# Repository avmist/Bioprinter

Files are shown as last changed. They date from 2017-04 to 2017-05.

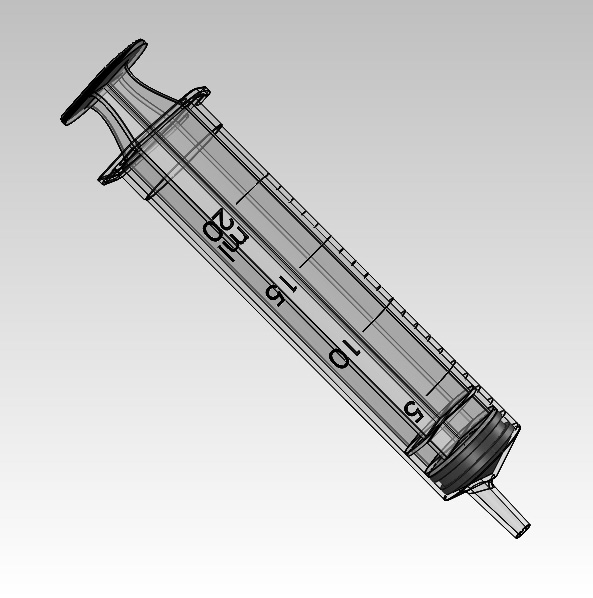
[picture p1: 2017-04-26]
Hardware/Design/Medical/Syringe plastipak-20ml-syringe/Renderings/syringe 20ml plastipak.png

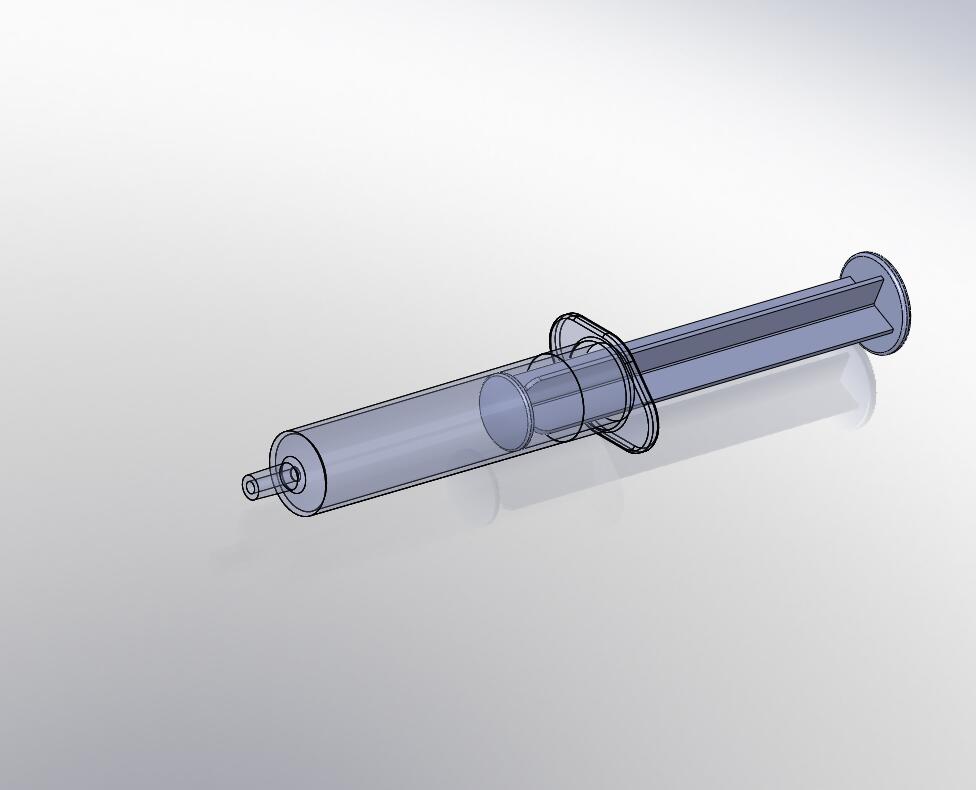
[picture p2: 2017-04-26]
Hardware/Design/Medical/5ml-syringe/Renderings/5ml hsw syringe .jpg

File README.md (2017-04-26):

Add your crew's remote repository, and call it upstream
git remote add upstream https://github.com/UCDBioe3090Blue/Bioprinter.git

Add the Bioe repository, call it headwaters (really, you can call it anything you want)
git remote add headwaters https://UCDBioe3090Blue@github.com/UCDBioe/Bioprinter.git

Pull the headwaters remote into your local repo
git pull headwaters master
git fetch headwaters master
git diff master headwaters/master
git diff --name-only master headwaters/master
git merge headwaters/master 

Pull the upstream remote into your local repo
git pull upstream master

Push updated local repo to origin
git push origin master

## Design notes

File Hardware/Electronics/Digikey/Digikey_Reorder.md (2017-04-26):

Bioprinter - BOM
================

## Digikey
-------------

Per Syringe Extruder
--------------------
Quantity  |   Part Number   |   Description                     
----------|-----------------|-----------------------------------
4         |  FQP30N06L-ND   |  MOSFET                           
4         |  DS18B20+-ND    |  TempSensor                       

Wire Harness
------------
Quantity  |   Part Number   |   Description                     
----------|-----------------|-----------------------------------
30        |  455-1130-1-ND  |  ZH_Connector_Socket              
10        |  455-1160-ND    |  ZH_Female                        
10        |  455-1658-ND    |  ZH_Male_pin_Solder               
30        |  WM2901-ND      |  Molex_3pos_female                
30        |  WM2562CT-ND    |  Molex_Connector_Socket_Crimp     
60        |  WM2513-ND      |  Molex_Connector_Socket_Crimp_Gold
30        |  WM2534-ND      |  Molex_3pos_male                  
30        |  WM2565CT-ND    |  Molex_Connector_Pin_Crimp        
60        |  WM2516-ND      |  Molex_Connector_Pin_Crimp_Gold   
30        |  WM2900-ND      |  Power_Plug                       
60        |  WM2512CT-ND    |  Female_Socket_Crimp              
30        |  WM2533-ND      |  Power_Housing_Male               
60        |  WM2515CT-ND    |  Male_Pin_Crimp                   
1         |  6820 BK005-ND  |  28AWG_Stranded_BLK               
1         |  6820 RD005-ND  |  28AWG_Stranded_RED               
1         |  6820 YL005-ND  |  28AWG_Stranded_YEL               
1         |  6823 BK005-ND  |  22AWG_Stranded_BLK               
1         |  6823 RD005-ND  |  22AWG_Stranded_RED               
1         |  6823 GR005-ND  |  22AWG_Stranded_GRN               
1         |  6823 BL005-ND  |  22AWG_Stranded_BLU               
20        |  WM2873-ND      |  Molex_StepperMotor_Connector     
80        |  WM2510-ND      |  Stepper_Motor_Connector_Terminal 
1         |  ASW40-25-ND    |  1/8in_Spiral_Wrap                

UV-LED
------
1         |  1125-1254-ND   |  30mA 365nm 
1         |  1214-1322-ND   |  A 365nm

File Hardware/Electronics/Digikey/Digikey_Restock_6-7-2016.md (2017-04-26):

Bioprinter - BOM
================

## Digikey
-------------

Per Syringe Extruder
--------------------
Quantity  |   Part Number   |   Description                     
----------|-----------------|-----------------------------------                        
4         |  DS18B20+-ND    |  TempSensor                       

Wire Harness
------------
Quantity  |   Part Number   |   Description                     
----------|-----------------|-----------------------------------           
20        |  WM2901-ND      |  Molex_3pos_female                     
30        |  WM2513-ND      |  Molex_Connector_Socket_Crimp_Gold
20        |  WM2534-ND      |  Molex_3pos_male                       
30        |  WM2516-ND      |  Molex_Connector_Pin_Crimp_Gold   
10        |  WM2900-ND      |  Power_Plug                       
20        |  WM2512CT-ND    |  Female_Socket_Crimp              
10        |  WM2533-ND      |  Power_Housing_Male               
20        |  WM2515CT-ND    |  Male_Pin_Crimp                   
1         |  6820 BK005-ND  |  28AWG_Stranded_BLK               
1         |  6820 RD005-ND  |  28AWG_Stranded_RED               
1         |  6820 YL005-ND  |  28AWG_Stranded_YEL               
1         |  6823 BK005-ND  |  22AWG_Stranded_BLK               
1         |  6823 RD005-ND  |  22AWG_Stranded_RED               
             
1         |  ASW40-25-ND    |  1/8in_Spiral_Wrap                

UV-LED
------
1         |  1125-1254-ND   |  30mA 365nm 
1         |  1214-1322-ND   |  A 365nm

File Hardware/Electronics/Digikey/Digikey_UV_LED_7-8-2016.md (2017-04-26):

Quantity  |   Part Number               |   Description                   
----------|-----------------------------|---------------------------------
2         |  1537-1032-ND               |  EMITTER UV 365NM 1A STAR       
2         |  1168-2129-ND               |  12x12x10 Ceramic Heatsink      
2         |  1284-1346-1-ND             |  Heat Spreader                  
1         |  MLX90614ESF-ACF-000-TU-ND  |  IR Temperature Sensor          
4         |  A98333-ND                  |  TERM BLOCK 2POS SIDE ENT 2.54MM
4         |  ED10561-ND                 |  CONN TERM BLOCK 2.54MM 2POS PCB

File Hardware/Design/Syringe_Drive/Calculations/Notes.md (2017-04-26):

Stepper Motor Spur Gear
-----------------------
Part Number: S10T08M012S0505
Pitch Diameter 9.6 mm
With Hub and Set screw
Module 0.8 teeth/mm
12 Teeth
20° Pressure Angle
303 Stainless Steel Gear
https://sdp-si.com/eStore/Catalog/Group/591#

Large Gear mates with Stepper Motor Spur Gear
---------------------------------------------

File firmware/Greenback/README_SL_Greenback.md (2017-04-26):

Changes and Notes for Bioprinter Greenback (Barlin)
=======================================

By Steve Lammers

Notes and Stuff To Do
=====================
*  **Fix printer bed size, currently too small**
*  **ADVANCE in stepper.cpp, use this to define a new method for BIOADVANCE**

Printer Details
===============
 *  AO-100 (not AO-101)
 *  RAMPS 1.4 board
 *  Arduino MEGA 2560 micro
 *  See link at LulzBot for [details](http://download.lulzbot.com/AO-100) 

Configure Greenback for AO-100 printer
===================================
AP-100 Printer is based on the RAMPS1.4 board with an extruder, bed and fan power. Change the following code in Configuration.h 

`BASIC SETTINGS: select your board type, temperature sensor type, axis scaling, and endstop configuration`

    // The following define selects which electronics board you have.
    // Please choose the name from boards.h that matches your setup
    #ifndef MOTHERBOARD
    //#define MOTHERBOARD BOARD_ULTIMAKER
    #define MOTHERBOARD BOARD_RAMPS_13_EFB
    #endif
    
The name 'BOARD_RAMPS_13_EFB' found in the boards.h file.

Baud Rate
---------
    // This determines the communication speed of the printer
    #define BAUDRATE 115200 //250000

Thermal Settings
----------------
    #define TEMP_SENSOR_0 7
    #define TEMP_SENSOR_1 0
    #define TEMP_SENSOR_2 0
    #define TEMP_SENSOR_BED 7

Mechanical Settings
-------------------
Set the direction that the stepper motors move the gantry

    #define INVERT_X_DIR false    // for Mendel set to false, for Orca set to true
    #define INVERT_Y_DIR true    // for Mendel set to true, for Orca set to false
    #define INVERT_Z_DIR false     // for Mendel set to false, for Orca set to true
    #define INVERT_E0_DIR true   // for direct drive extruder v9 set to true, for geared extruder set to false
    #define INVERT_E1_DIR false    // for direct drive extruder v9 set to true, for geared extruder set to false
    #define INVERT_E2_DIR false   // for direct drive extruder v9 set to true, for geared extruder set to false

Define endstop inverting

    // The pullups are needed if you directly connect a mechanical endswitch between the signal and ground pins.
    const bool X_MIN_ENDSTOP_INVERTING = false; // set to true to invert the logic of the endstop.
    const bool Y_MIN_ENDSTOP_INVERTING = false; // set to true to invert the logic of the endstop.
    const bool Z_MIN_ENDSTOP_INVERTING = false; // set to true to invert the logic of the endstop.
    const bool X_MAX_ENDSTOP_INVERTING = false; // set to true to invert the logic of the endstop.
    const bool Y_MAX_ENDSTOP_INVERTING = false; // set to true to invert the logic of the endstop.
    const bool Z_MAX_ENDSTOP_INVERTING = false; // set to true to invert the logic of the endstop.

Define manual homing position

    // The position of the homing switches
    #define MANUAL_HOME_POSITIONS  // If defined, MANUAL_*_HOME_POS below will be used
    //#define BED_CENTER_AT_0_0  // If defined, the center of the bed is at (X=0, Y=0)

Endstop Config
--------------
    #define min_software_endstops true // If true, axis won't move to coordinates less than HOME_POS.
    #define max_software_endstops true  // If true, axis won't move to coordinates greater than the defined lengths below.
    
    // Travel limits after homing
    #define X_MAX_POS 200
    #define X_MIN_POS 0
    #define Y_MAX_POS 190
    #define Y_MIN_POS 0
    #define Z_MAX_POS 100
    #define Z_MIN_POS 0

Axis Scaling
------------
    #define DEFAULT_AXIS_STEPS_PER_UNIT   {44.7,44.7,1512,800}  // default steps per unit for Ultimaker
    #define DEFAULT_MAX_FEEDRATE          {800, 800, 10, 500}    // (mm/sec)
    #define DEFAULT_MAX_ACCELERATION      {9000,9000,100,10000}    // X, Y, Z, E maximum start speed for accelerated 

Flashing the Firmware
======================
 *  Use Arduino 1.0.1 or 1.0.5
 *  Use Arduino MEGA 2560 board
 *  Use correct Greenback version for the AO-100 printer
 *  Electronics board in the Configuration.h set to 33 (RAMPS 1.3 = 33 (Power outputs: Extruder, Bed, Fan))
 *  In Configuration.h: #define DEFAULT_AXIS_STEPS_PER_UNIT   {50.25,50.25,756.00,408.00}  // default steps per unit for ultimaker 
 *  May need to set X_MAX_LENGTH, etc for the size of the bed????
 *  Need to use current version of Greenback if we are going to use multiple extruders!!!!!!!!!!!!!!!!!

Pin Definitions for Test LED
============================
###In pinsBioprinter.h

E0 LED Pin is on Aux-4 pin 3: `#DEFINE E0_LED_PIN 32 // Digital Pin 32 on AUX-4` 

###In Greenback_main.cpp

Initialize Pins: `pinMode(E0_LED_PIN, OUTPUT);`

###In Stepper.cpp and Stepper.h

Define WRITE_E_LED() to toggle LED during extrusion

Configure for BioExtruders
=============================
###In Configuration.h
* define BIOEXTRUDERS 2 // Defines the number of bioextruders

Copy and alter Stepper.h and Stepper.cpp to BioValve.h and BioValve.cpp

In pinsBioprinter.h
`define BIOPRINT 1 // 1-enables bioprint, 0-enables filament`
Set BIOPRINT to 1 when a bioprint tool is selected, set it to 0 when a filament tool is selected

In Greenback_main.cpp: Define tools T0-T9 as filament extruders and T10-T19 as bio-print heads. When T0-T9 is selected set BIOPRINT = 0, when T10-T19 is selected set BIOPRINT to 1.

Use BIOPRINT to govern how extrusion is done in stepper.cpp and stepper.h. Since this contains the ISR which is used in all of the printing, keep using G1 E codes for printing. Change to bioprint heads using T codes, and flag what material is being printed (bio or plastic) using BIOPRINT.

plan_buffer_line()
===================
`void plan_buffer_line(const float &x, const float &y, const float &z, const float &e, float feed_rate, const uint8_t &extruder)`

target[]: rounded total steps in x,y,z,e-direction
`target[X_AXIS] = lround(x*axis_steps_per_unit[X_AXIS]);`

Prevent dangerous extrude code follows

define total absolute steps to move stepper motors for each axis i.e.:
`block->steps_x = labs(target[X_AXIS]-position[X_AXIS]);`

`block->steps_e` has some additional code, basically: `steps_e/(pi R^2)*100/100` where R is filament diameter, basically normalizes thin and thick filament feedrates. **Will need to add to this for bioprinter**

```
  block->steps_e = labs(target[E_AXIS]-position[E_AXIS]);
  block->steps_e *= volumetric_multiplier[active_extruder];
  block->steps_e *= extrudemultiply;
  block->steps_e /= 100;
```

step_event_count is the max step size for x,y,z,e directions 
`block->step_event_count = max(block->steps_x, max(block->steps_y, max(block->steps_z, block->steps_e)));`

Fan Speed `block->fan_speed = fanSpeed;`

Stuff for BAEICUDA

```
  #ifdef BARICUDA
  block->valve_pressure = ValvePressure;
  block->e_to_p_pressure = EtoPPressure;
  #endif
```
Compute direction bits for this block `block->direction_bits = 0;`, then shift in bits in the LSB for X,Y,Z,E direction 0 or 1

Set active extruder
`block->activer_extruder = extruder;`

Ennable active axes

```
  if(block->steps_x != 0) enable_x();
  if(block->steps_y != 0) enable_y();
```

Enable extruder(s)
This code ensures that only the active extruder is enabled if DISABLE_INACTIVE_EXTRUDER is defined (which it is by default). **Will need to add to this for bioprinters?**

Calculate the total length of the movement. For cartesian bots, the `X_AXIS` is the real X movement and same for `Y_AXIS`.

```
  float delta_mm[4];
  delta_mm[X_AXIS] = (target[X_AXIS]-position[X_AXIS])/axis_steps_per_unit[X_AXIS];
  delta_mm[Y_AXIS] = (target[Y_AXIS]-position[Y_AXIS])/axis_steps_per_unit[Y_AXIS];
  delta_mm[Z_AXIS] = (target[Z_AXIS]-position[Z_AXIS])/axis_steps_per_unit[Z_AXIS];
  delta_mm[E_AXIS] = ((target[E_AXIS]-position[E_AXIS])/axis_steps_per_unit[E_AXIS])*volumetric_multiplier[active_extruder]*extrudemultiply/100.0;
  if ( block->steps_x <=dropsegments && block->steps_y <=dropsegments && block->steps_z <=dropsegments )
  {
    block->millimeters = fabs(delta_mm[E_AXIS]);
  } 
  else
  {
    block->millimeters = sqrt(square(delta_mm[X_AXIS]) + square(delta_mm[Y_AXIS]) + square(delta_mm[Z_AXIS]));
  {
  float inverse_millimeters = 1.0/block->millimeters;  // Inverse millimeters to remove multiple divides 

    // Calculate speed in mm/second for each axis. No divide by zero due to previous checks.
  float inverse_second = feed_rate * inverse_millimeters;

  int moves_queued=(block_buffer_head-block_buffer_tail + BLOCK_BUFFER_SIZE) & (BLOCK_BUFFER_SIZE - 1);
```

In configuration.h, SLOWDOWN defined as default. inverse_second is redeined to slow down when the look ahead
buffer is only half full

Calculate the speedin mm/sec and the step-rate in step/sec

```
block->nominal_speed = block->millimeters * inverse_second; // (mm/sec) Always > 0
block->nominal_rate = ceil(block->step_event_count * inverse_second); // (step/sec) Always > 0
```

Calculate `current_speed` in mm/sec for each axis and `speed_factor <=1` for the minimum of either 1 or max_feedrate/current_speed

XY_FREQUENCY_LIMIT not defined by default

Speed is corrected using speed_factor

```
  // Correct the speed  
  if( speed_factor < 1.0)
  {
    for(unsigned char i=0; i < 4; i++)
    {
      current_speed[i] *= speed_factor;
    }
    block->nominal_speed *= speed_factor;
    block->nominal_rate *= speed_factor;
  }
```

Calculate acceleration and save to block

```
block->acceleration_st
block->acceleration
block->acceleration_rate
```

Correct for jerking due to high acceleration

```
block->max_entry_speed
block->entry_speed
block->normal_length_flag
block->recalculate_flag
```

Calculate trapezoid for the block, move buffer head, update position and wake up the stepper motors

```
calculate_trapezoid_for_block(block, block->entry_speed/block->nominal_speed,
safe_speed/block->nominal_speed);

// Move buffer head
block_buffer_head = next_buffer_head;

// Update position
memcpy(position, target, sizeof(target)); // position[] = target[]

planner_recalculate();

st_wake_up();
```
st_wake_up called in stepper.cpp
***END PLAN BUFFER LINE***

Timers
======
Timers all have something in Greenback_main.cpp
* Timer0 ????? Pins 1 and 26
* Timer1 - stepper.cpp
* Timer2 ????? Pins 16 and 23 are open on AUX-4
* Timer3 - servo.h
* Timer4 - servo.h
* Timer5 - servo.h

Extruder Offsets
================
Need to figure out how to have the firmware apply offsets for each of the bio-extruders.

```
// Offset of the extruders (uncomment if using more than one and relying on firmware to position when changing).
// The offset has to be X=0, Y=0 for the extruder 0 hotend (default extruder).
// For the other hotends it is their distance from the extruder 0 hotend.
#define EXTRUDER_OFFSET_X {0.0, 10.00} // (in mm) for each extruder, offset of the hotend on the X axis
#define EXTRUDER_OFFSET_Y {0.0, 5.00}  // (in mm) for each extruder, offset of the hotend on the Y axis
```

In Greenback_main.cpp

```
// Extruder offset
#if EXTRUDERS > 1 || defined(BIOEXTRUDERS) //SL Note: Added BIOEXTRUDERS to account for offset
#ifndef DUAL_X_CARRIAGE
  #define NUM_EXTRUDER_OFFSETS 2 // only in XY plane
#else
  #define NUM_EXTRUDER_OFFSETS 3 // supports offsets in XYZ plane
#endif
//float extruder_offset[NUM_EXTRUDER_OFFSETS][EXTRUDERS] = {
float extruder_offset[NUM_EXTRUDER_OFFSETS][10+BIOEXTRUDERS] = { //SL Note: Added 10 to account for Filament extruders 0-9
#if defined(EXTRUDER_OFFSET_X) && defined(EXTRUDER_OFFSET_Y)
  EXTRUDER_OFFSET_X, EXTRUDER_OFFSET_Y 
#endif
};
```

So `extruder_offset` is a 3xn array where n = 10+BIOEXTRUDERS. BIOEXTRUDERS is the number of bioextruders, 10+ is the number of possible filament printheads. Of course this is much higher than the actual number the RepRap could support, but it was chosen such the T10 would be the first bioprint head. So to make this work, fill in the `EXTRUDER_OFFSET_X` and `EXTRUDER_OFFSET_Y` arrays in Configuration.h

```
#define EXTRUDER_OFFSET_X {0.0, 0.0, 0.0, 0.0, 0.0, 0.0, 0.0, 0.0, 0.0, 0.0, 10.0} // (in mm) for each extruder, offset of the hotend on the X axis
#define EXTRUDER_OFFSET_Y {0.0, 0.0, 0.0, 0.0, 0.0, 0.0, 0.0, 0.0, 0.0, 0.0, 5.00}  // (in mm) for each extruder, offset of the hotend on the Y axis
```

Now when the tool is changed, say to bioprinthead[0] using T10 command, the `current_position` array is updated to reflect the new printhead. So if `EXTRUDER_OFFSET_X[10]=10` and `current_position[0]=100` before the tool was changed, after issuing T10 command `current_position=110`, because `EXTRUDER_OFFSET_X[10]=10`. However, the printer stage does not move, the position will be reflected at the next move command. If you want to change printheads and begin printing at the same point with the new printhead, you will need to resend the position command using G1.

Removal of Existing Extruder
=============================
The existing extruder and part heating pad needs to be removed. When the extruder heater is disconnected, the printer throws an error "Printer stopper due to errors. Fix the error and use M999 to reset. (Temperature is reset. Set it after restatring)". This happened because the Stop() function was called. To correct this, use an existing override by adding the following to pinsBioprinter.h

'''
// This definition is used to turn off the physical checks on thermister
// readings, typically set in pins.h. T0 and T1 thermistors provided temperature data for
// the extruder and heated bed respectively. These thermistors are disconnected
// for the bioprinter. So we can ignore the associated errors using this definition
#define BOGUS_TEMPERATURE_FAILSAFE_OVERRIDE
// Temperature errors persist, set TEMP_SENSOR_0 = 0 AND TEMP_SENSOR_BED = 0 in Configuration.h
'''

Temperature errors persist. Set in Configuration.h

'''
#define TEMP_SENSOR_0 0 // 7 Setting for Lulzbot AO-100
#define TEMP_SENSOR_1 0
#define TEMP_SENSOR_2 0
#define TEMP_SENSOR_BED 0 // 7 Setting for Lulzbot AO-100
'''

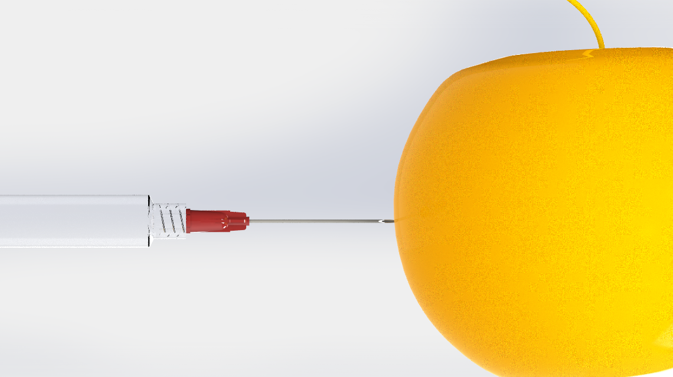
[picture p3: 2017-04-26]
Hardware/Design/Medical/hypodermic-syringe-1.snapshot.3/Renderings/syringe apple.PNG

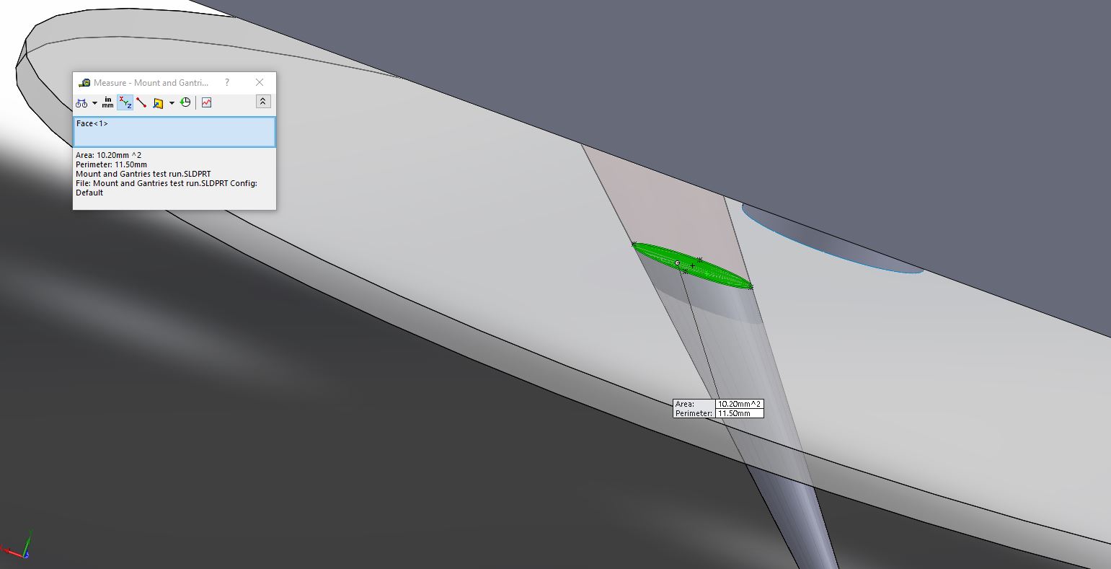
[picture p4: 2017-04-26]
Hardware/Design/Needle_Mount/Square_Carrige/IR sensor area covered.JPG

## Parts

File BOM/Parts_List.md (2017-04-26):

---------------------------------------------------
Additional Optional Equipment not Purchased for This Model
==========================
***
Digital Pressure Regulator
==========================
###[IPV-2010RC](http://www.smcpneumatics.com/ITV2010-31N2N4.html) - Digital pressure sensor
* Min supply pressure: .1 MPa (14.5 psi)
* Max supply pressure: .2 MPa
* Set pressure range: .005 - .1 MPa (0.725 - 14.5 psi)
* Input Signal: 0-5 VDC or RS-232
* Minimum Digit: 0.1 psi
* Accuracy: 0.2% Full Span +/- 1 digit
	* 0.002 * (14.5 - 0.725)psi = 0.03psi

###[IPV-1000](http://www.smcpneumatics.com/ITV2010-31N2N4.html) - Digital pressure sensor
* Min supply pressure: .1 MPa (14.5 psi)
* Max supply pressure: .2 MPa
* Set pressure range: .001 - .1 MPa (0.145 - 14.5 psi)
* Input Signal: 0-5 VDC ***only***
* Minimum Digit: 0.1 psi
* Accuracy: 0.2% Full Span +/- 1 digit
	* (.002 * (14.5 - 0.145)psi) = 0.02psi

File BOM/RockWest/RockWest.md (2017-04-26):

Bioprinter - BOM
================

## Rock West Composites
-----------------------

Carbon Fiber Sleeves for Tubing Heaters
---------------------------------------
Quantity  |  Part Number  |  Description                             
----------|---------------|------------------------------------------
10        |  BR-C-050     |  Dry Braided Sleeve - Carbon Fiber - 0.5"

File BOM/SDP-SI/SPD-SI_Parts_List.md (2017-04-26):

SDP-SI - BOM
============
## For Each Syringe Drive
-------------------------

Quantity  |  Part Number       |  Description                                                                                      
----------|--------------------|---------------------------------------------------------------------------------------------------
1         |  A 7X 1-06012      |  .18720" (+.000/-.0002) Dia. 1.25" Long 303 Stainless Steel Shaft                                 
2         |  A 7X 1-04023      |  .12470" (+.000/-.0002) Dia. 2.375" Long 303 Stainless Steel Shaft                                
1         |  A 7X 8-C04031     |  0.125" I.D. 0.1875" O.D. 0.031" Thick Shaft Spacer                                               
3         |  A 7X 8-C04016     |  0.125" I.D. 0.1875" O.D. 0.016" Thick Shaft Spacer                                               
1         |  S5000Y-12510      |  0.1248" Bore 0.3125" O.D. 0.18" Wide 303 Stainless Steel Collar Style                            
1         |  A 1T 2-Y32016     |  32 DP 16 Teeth 20° Pressure Angle Acetal / Brass insert spur Gear                                
1         |  S1C83Z-P048B055S  |  55:1 Gear Ratio 55 Teeth Worm Gear                                                               
1         |  S1D94Z-P048SS     |  48DP/1 Lead/.33PD 20° Pressure Angle Stainless Steel Worm                                        
1         |  S1063Z-048A024    |  48 D.P. 24 Teeth 20° Pressure Angle AGMA Q10 Quality With ( Hub / S.S.) 2024 Aluminum Alloy Gear.
1         |  S1063Z-048S048    |  48 D.P. 48 Teeth 20° Pressure Angle AGMA Q10 Quality With ( Hub / S.S.) 303 Stainless Steel Gear.

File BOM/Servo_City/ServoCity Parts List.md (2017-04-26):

Servo City - BOM
================
## For Each Syringe Drive
-------------------------

Mostly Actobotics Parts are needed. Some of the gears are not available on Servo City. These components were sourced from SDP/SI

Quantity  |  Part Number  |  Description                                      |  Unit Price  |  Total 
----------|---------------|---------------------------------------------------|--------------|--------
1         |  585442       |  3.00 inch Aluminum Channel                       |  3.99        |  3.99  
1         |  555152       |  Stepper Motor Mount (NEMA 17)                    |  7.49        |  7.49  
1         |  625176       |  3/16 inch to 5mm Set Screw Shaft Coupler         |  4.99        |  4.99  
1         |  634136       |  3/16 inch x1 inch Precision Shaft                |  0.49        |  0.49  
1         |  634138       |  3/16 inch x2 inch Precision Shaft                |  0.69        |  0.69  
2         |  633138       |  Center Hole Adaptors (4 pack)                    |  1.99        |  3.98  
2         |  535206       |  1/8 inch ID x 3/8 inch OD Ball Bearing (2 pack)  |  1.99        |  3.98  
1         |  545424       |  90 Degree Quad Hub Mount B                       |  4.99        |  4.99  
1         |  585656       |  Beam Bracket T (Pair)                            |  1.49        |  1.49  
1         |  585600       |  Beam Attachment Block B (4 pack)                 |  4.99        |  4.99  
1         |  585416       |  6.16 inch Aluminum Beam (2 pack)                 |  5.49        |  5.49  
1         |  615410       |  32P Beam Gear Rack                               |  5.99        |  5.99  
2         |  585434       |  1 inch Bore Tube Clamp A                         |  5.99        |  11.98 
1         |  585612       |  Beam Bracket F (Pair)                            |  1.49        |  1.49  
1         |  585404       |  1.54 inch Aluminum Beam (2 pack)                 |  2.39        |  2.39  
1         |  585490       |  Beam Crossover Adaptor A                         |  2.99        |  2.99  
1         |  585400       |  Attachment Blocks (12 pack)                      |  9.99        |  9.99  
1         |  545360       |  90 Degree Quad Hub Mount C                       |  5.99        |  5.99  
1         |  632146       |  Actobotics Hardware Pack A                       |  39.99       |  39.99 
1         |  632148       |  Hardware Pack B                                  |  10.99       |  10.99 
4         |  534-3488     |  6-32x .750 inch Aluminum Standoffs (Round)       |  0.45        |  1.80

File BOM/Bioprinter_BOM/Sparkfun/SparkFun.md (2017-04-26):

Bioprinter - BOM
================

## Spark Fun
-------------

Per Syringe Extruder
--------------------
Quantity  |  Part Number  |  Description                                    
----------|---------------|-------------------------------------------------
1         |  COM-10080    |  Thermoelectric Cooler 40x40mm                  
1         |  COM-11288    |  Heating Pad - 5x10cm                           
5         |  PRT-09915    |  JSST Jumper 3 Wire Assembly                    
1         |  PRT-10811    |   DC Barrel Jack Adapter - Breadboard Compatible
5         |  SEN-08733    |  Infrared Sensor Jumper Wire 3-Pin JST

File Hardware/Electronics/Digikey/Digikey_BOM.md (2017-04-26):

Bioprinter - BOM
================

## Digikey
-------------

Per Syringe Extruder
--------------------
Quantity  |   Part Number   |   Description                     
----------|-----------------|-----------------------------------
4         |  FQP30N06L-ND   |  MOSFET                           
1         |  438-1046-ND    |  Breadboard                       
4         |  DS18B20+-ND    |  TempSensor                       
1         |  1050-1041-ND   |  Arduino_UNO                      
1         |  T1171-P5RP-ND  |  Power_Adapter_5V_3.6A            
1         |  839-1219-ND    |  Barrel_Jack_to_Gator

Wire Harness
------------
Quantity  |   Part Number   |   Description                     
----------|-----------------|-----------------------------------
30        |  455-1130-1-ND  |  ZH_Connector_Socket              
10        |  455-1160-ND    |  ZH_Female                        
10        |  455-1658-ND    |  ZH_Male_pin_Solder               
30        |  WM2901-ND      |  Molex_3pos_female                
30        |  WM2562CT-ND    |  Molex_Connector_Socket_Crimp     
60        |  WM2513-ND      |  Molex_Connector_Socket_Crimp_Gold
30        |  WM2534-ND      |  Molex_3pos_male                  
30        |  WM2565CT-ND    |  Molex_Connector_Pin_Crimp        
60        |  WM2516-ND      |  Molex_Connector_Pin_Crimp_Gold   
30        |  WM2900-ND      |  Power_Plug                       
60        |  WM2512CT-ND    |  Female_Socket_Crimp              
30        |  WM2533-ND      |  Power_Housing_Male               
60        |  WM2515CT-ND    |  Male_Pin_Crimp                   
1         |  6820 BK005-ND  |  28AWG_Stranded_BLK               
1         |  6820 RD005-ND  |  28AWG_Stranded_RED               
1         |  6820 YL005-ND  |  28AWG_Stranded_YEL               
1         |  6823 BK005-ND  |  22AWG_Stranded_BLK               
1         |  6823 RD005-ND  |  22AWG_Stranded_RED               
1         |  6823 GR005-ND  |  22AWG_Stranded_GRN               
1         |  6823 BL005-ND  |  22AWG_Stranded_BLU               
20        |  WM2873-ND      |  Molex_StepperMotor_Connector     
80        |  WM2510-ND      |  Stepper_Motor_Connector_Terminal 
1         |  ASW40-25-ND    |  1/8in_Spiral_Wrap                

Extras
------
1         |  1050-1018-ND   |  ArduinoMega                      
1         |  Q2F1-KIT-ND    |  HeatShrink_Kit                   
1         |  8331S-15G      |  Conductive Epoxy 10min work time 

Peltier
-------
1         |  ATS1758-ND     |  Heat Sink 
1         |  3M12011-ND     |  Thermal Tape 

Blower
------
1         |  603-1370-ND    |  Squirrel Cage Blower 

UV-LED
------
1         |  1125-1254-ND   |  30mA 365nm 
1         |  1214-1322-ND   |  A 365nm 

Also Needed
------------------------------
* Engineer PA-09 Crimp tool
* Paladin Grip P20 Wire Stripper

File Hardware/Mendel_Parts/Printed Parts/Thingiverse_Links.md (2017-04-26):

Parts on Thingiverse
--------------------
* [X-carrige](hrome-extension://hdokiejnpimakedhajhdlcegeplioahd)
* [Frame Brackets](http://www.thingiverse.com/thing:97575)

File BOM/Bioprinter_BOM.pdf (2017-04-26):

ID | Part Name | Vendor Number | Quantity | Description | Photo

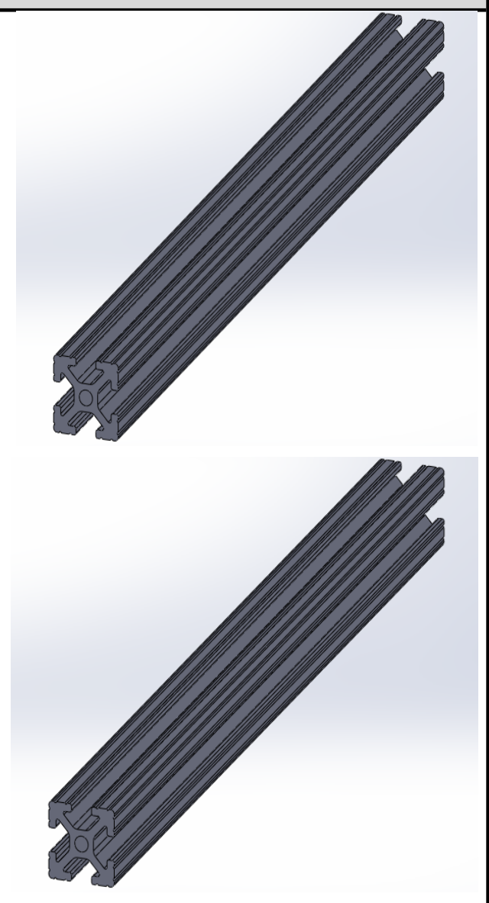
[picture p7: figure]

A1

Aluminum Extrusion
80/20 Size 20-2020
Cut to 265 mm long
Tapped M5 x 0.8 bolt

Misumi
HFS5-2020-265-TPW 4

T-Slotted Frame
Shortest
(x-axis)

A2

Aluminum Extrusion
80/20 Size 20-2020
Cut to 300 mm long
Tapped M5 x 0.8 bolt

Misumi
HFS5-2020-300-TPW 4

T-Slotted Frame
2nd Shortest
(yz-axis)

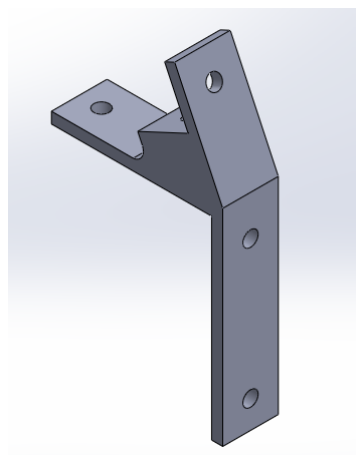
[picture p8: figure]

A3 | Lower Middle Vertex | 3D Printer N/A | 4 | Middle Bracket (x-axis)
A4 | M5 x 10 Bolt,
SHCS Black-oxide

McMaster-Carr
91239A224 | 12 | M5 x 10 Bolt
A5 | M5 Washer,
Steel, Zinc Plated

McMaster-Carr
91166A240 | 16 | M5 Washer

A6

80/20
Slide-In Economy
TNut M5 Thread

Misumi
HNKK5-5 | 25 | T-Nut
A7 | M5 x 14 Bolt,
SHCS Black-Oxide

McMaster-Carr
91290A230 | 4 | M5 x 14 Bolt

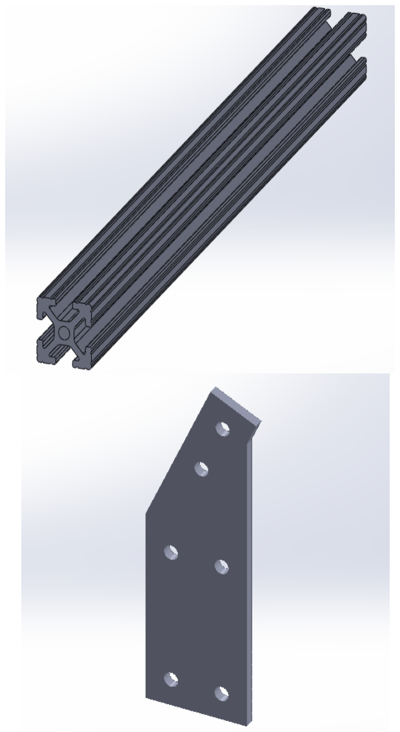
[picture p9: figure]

B1

Aluminum Extrusion
80/20 Size 20-2020
Cut to 380 mm long
Tapped M5 x 0.8 bolt

McMaster-Carr
HFS5-2020-380-TPW 4

T-Slotted Frame
2nd Longest
(y-axis)
B2 | Lower Left-Right
Vertex | 3D Printer N/A | 4

Left/Right Bottom
Corners
(y-axis)

A4 M5 x 10 Bolt,
SHCS Black-Oxide

McMaster-Carr
91290A115 | 28 | M5 x 10 Bolt
A5 | M5 Washer,
Steel, Zinc Plated

McMaster-Carr
91166A240 | 28 | M5 Washer

A6

80/20 Slide-In
Economy
TNut M5 Thread

Misumi
HNKK5-5 | 28 | T-Nut

C1

Aluminum Extrusion
80/20 Size 20-2020
Cut to 385 mm long
Tapped M5 x 0.8 bolt
Horz Drilled Holes

Misumi
HFS5-2020-385-TPW-AH70-BH315

2

T-Slotted Frame
Longest
(x-axis)
C2 | Z Upper Idler | 3D Printer
N/A | 2 | Upper Mount
(z-axis)

C3 M5 x 16 Bolt,
BHCS Black-Oxide

McMaster-Carr
91239A232 | 4 | M5 x 16 Bolt
A4 | M5 x 10 Bolt,
SHCS Black-Oxide

McMaster-Carr
91290A115 | 8 | M5 x 10 Bolt
A5 | M5 Washer,
Steel, Zinc Plated

McMaster-Carr
91166A240 | 8 | M5 Washer

A6

80/20 Slide-In
Economy
TNut M5 Thread

Misumi
HNKK5-5 | 5 | T-Nut

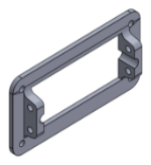
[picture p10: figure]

D1 | Y Rod Mount | 3D Printer
N/A | 2 | Rod Mount
(y-axis)
D2 | 8mm rod
(5/16" drill rod) 36"

Fastenal

47768 | 2 | Steel Rod (y-axis)
D3 | Z Rod Clamp | 3D Printer
N/A | 4 | Clamp
(z-axis)

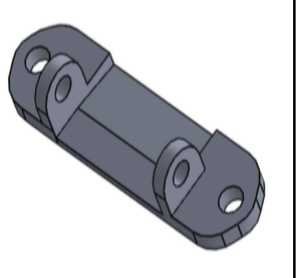
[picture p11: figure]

D4 | Y Tensioner Mount | 3D Printer
N/A | 1 | Idler Mount
(y-axis)
D5 | Y Idler Tensioner | 3D Printer
N/A | 1 | Idler Tensioner
(y-axis)

D6 LM8UU Bearing
Holder

3D Printer
N/A | 4 | Bearing Mount

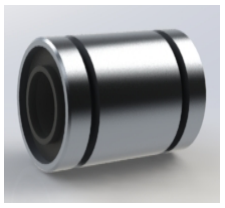
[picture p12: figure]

D7 | 12x LM8UU Linear
Bearings

Amazon
0601227135386 | 4 | Bearings
D8 | 608ZZ Bearings | Amazon
0793200418750 | 4 | Bearings
D9 | Y Motor Mount | 3D Printer
N/A | 1 | Motor Mount
(y-axis)

D10

Nema 17 Stepper
Motor
2 A 45 Ncm (64oz.in)

Amazon

17HS16-2004S1 | 1 | Nema 17 Stepper Motor

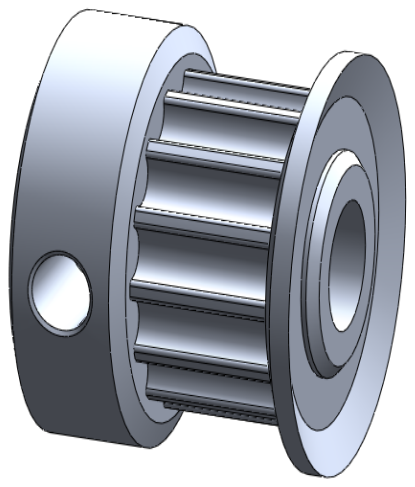
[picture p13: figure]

D11

2x Aluminum GT2 16T
Pulley
and
2M Belt for RepRap
3D printer Prusa i3

Amazon
0087169815683
6907496758795
1 | 16T Pulley

D12

2x Aluminum GT2 16T
Pulley
and
2M Belt for RepRap
3D printer Prusa i3

Amazon
0087169815683
6907496758795
1 | 2M Belt
D13 | Base Stage Plate

Custom Machine
Fabrication
N/A
1 | N/A
D14 | Belt Clamp | 3D Printer
N/A | 2 | Belt Clamp
(y-axis)

D15 M8 x 30 Bolt,
SHCS Black-Oxide

McMaster-Carr
91290A434 | 1 | M8 x 30 Bolt

D16 | M8 Nut Nyloc | McMaster-Carr
90576A117 | 1 | M8 Nut
D17 | M5 Nut | McMaster-Carr
90591A146 | 18 | M5 Nut
D18 | M3 x 10 Bolt,
SHCS Black-Oxide

McMaster-Carr
91290A115 | 14 | M3 x 10 Bolt
D19 | M3 Washer,
Steel, Zinc Plated

McMaster-Carr
91166A210 | 14 | M3 Washer
A4 | M5 x 10 Bolt,
SHCS Black-oxide

McMaster-Carr
91239A224 | 12 | M5 x 10 Bolt
A5 | M5 Washer,
Steel, Zinc Plated

McMaster-Carr
91166A240 | 16 | M5 Washer

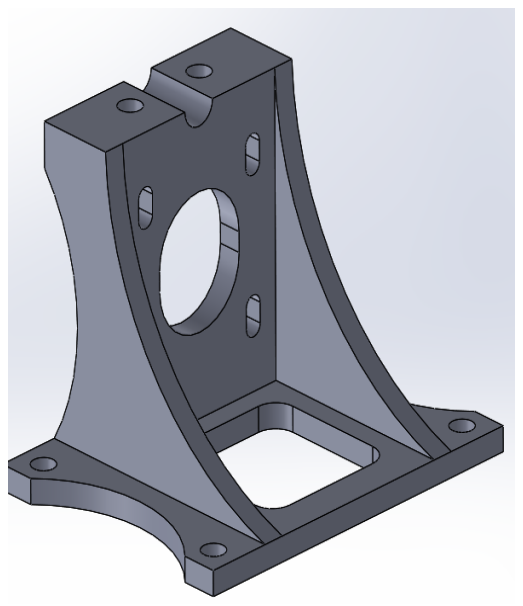
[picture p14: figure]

E1 | Lower Z Motor Mount | 3D Printer
N/A | 2

Lower Motor
Mount
(z-axis)
E2 | Beefy Coupler | 3D Printer
N/A | 2 | Beefy Coupler
(z-axis)

E3 M3 x 20 Bolt,
SHCS Black-Oxide

McMaster-Carr
91290A123 | 10 | M3 x 20 Bolt
E4 | M3 Nylon Lock Nut | McMaster-Carr
90576A102 | 12 | M3 Lock Nut


E5 Lower Z Mount Clamp | 3D Printer
N/A | 2

Lower Mount
Clamp
(z-axis)

E6 | Upper Z Motor Mount | 3D Printer N/A | 1

Upper Motor
Mount
(z-axis)
E7 | Upper Z Idle Mount | 3D Printer
N/A | 1 | Upper Idle Mount
(z-axis)


E8 | 8mm rod
(5/16" drill rod) 36"

Fastenal

47768 | 2 | Steel Rod (z-axis)

E9

Leadscrews -
3/8-12 Thread, 6 Ft.
Long,
Left Hand, Acme
Threaded Rod

MSC Industrial Supply

4354635 | 2 | Threaded Steel Rods
E10 | M3 x 16 Bolt,
SHCS Black-Oxide

McMaster-Carr
91290A120 | 12 | M3 x 16 Bolt

E11 | M3 Nut | McMaster-Carr
90592A009 | 10 | M3 Nut
E12 | M8 Washer | McMaster-Carr
91166A270 | 1 | M8 Washer
E13 3/8-12 ACME Hex Nut | McMaster-Carr
95155A111 | 2 | Hex Nut
E14 | Z Emergency Stop | 3D Printer
N/A | 1 | Emergency Stop
(z-axis)
A5 | M5 Washer,
Steel, Zinc Plated

McMaster-Carr
91166A240 | M5 Washer

A7 M5 x 14 Bolt,
SHCS Black-Oxide

McMaster-Carr
91290A230 | M5 x 14 Bolt


D3 | Z Rod Clamp | 3D Printer
N/A | 4 | Clamp
(z-axis)

D6 LM8UU Bearing
Mount

3D Printer
N/A | 4 | Bearing Mount
D7 | 12x LM8UU Linear
Bearings

Amazon
0601227135386 | 4 | Bearings
D8 | 608ZZ Bearings | Amazon
0793200418750 | 4 | Bearings

D10

Nema 17 Stepper
Motor
2 A 45 Ncm (64oz.in)

Amazon

17HS16-2004S1 | 1 | Nema 17 Stepper Motor


D11

2x Aluminum GT2 16T
Pulley
and
2M Belt for RepRap
3D printer Prusa i3

Amazon
0087169815683
6907496758795
1 | 16T Pulley
D15 | M8 x 30 Bolt,
SHCS Black-Oxide

McMaster-Carr
91290A434 | 1 | M8 x 30 Bolt
D16 | M8 Nut Nyloc | McMaster-Carr
90576A117 | 1 | M8 Nut

F1 | 8mm rod
(5/16" drill rod) 36" | Fastenal 47768 | 2 | Steel Rod (x-axis)
F2 | Stabilized X-Carriage | 3D Printer
N/A | 1 | Printer Stage Plate


F3 | M3 Threaded Insert | McMaster-Carr
94180A333 | 10 | Threaded Inserts
D6 | LM8UU Bearing
Mount

3D Printer
N/A | 4 | Bearing Mount


D7 | 12x LM8UU Linear
Bearings

Amazon
0601227135386 | 4 | Bearings

D12

2x Aluminum GT2 16T
Pulley
and
2M Belt for RepRap
3D printer Prusa i3

Amazon
0087169815683
6907496758795
1 | 2M Belt
D14 | Belt Clamp | 3D Printer
N/A | 2 | Belt Clamp
(x-axis)
D19 | M3 Washer,
Steel, Zinc Plated McMaster-Carr 91166A210 14 | M3 Washer
E10 | M3 x 16 Bolt,
SHCS Black-OxideMcMaster-Carr 91290A120 12 | M3 x 16 Bolt

G1 | RAMPS Mount | 3D Printer
N/A | 1 | RAMPS Mount
A4 | M5 x 10 Bolt,
SHCS Black-oxide

McMaster-Carr
91239A224 | 2 | M5 x 10 Bolt
A5 | M5 Washer,
Steel, Zinc Plated

McMaster-Carr
91166A240 | 2 | M5 Washer

H1 Large Stage Plate

Custom Machine
Fabrication
N/A
1 | Printer Stage Plate
H2 | Small Stage Plate

Custom Machine
Fabrication
N/A

2 Printer Stage Plate


H3

Compression Spring -
0.360OD,
0.032 music wire,
1.000 overall length

w.b. Jones Spring Co
Inc
C12-032-032
8 | Springs

H4

6-32 x .750 inch
Aluminum Standoffs
(Round)

Servo City
534-3488 | 8 | Spacer
H5 | 6-32 x 1" Bolt

Servo City
Actobotics Hardware
Pack A (632146)
Pack B (632148)

8 6-32 x 1" Bolt

A4 M5 x 10 Bolt,
SHCS Black-oxide

McMaster-Carr
91239A224 | 4 | M5 x 10 Bolt
A5 | M5 Washer,
Steel, Zinc Plated

McMaster-Carr
91166A240 | 4 | M5 Washer
D17 | M5 Nut | McMaster-Carr
90591A146 | 4 | M5 Nut

I1 Dry Braided Sleeve
Carbon Fiber - 0.5"

RockWest
BR-C-050 | 1

Carbon Fiber
Sleeves
for Tubing Heaters

I2 22 AWG (7/36) BC
6820

AlphaWire 22 AWG
(7/36) BC
6820
1 | 22 AWG Copper Wire
I3 | CONN HOUSING
2POS .100 W/LATCH

DigiKey
WM2900-ND | 3 Male 2 POS wire housing
I4 | CONN HOUSING
3POS .100 W/LATCH

DigiKey
WM2901-ND | 2 Male 3 POS wire housing
I5 | CONN HOUSING
3POS .100 SINGLE

DigiKey


WM2801-ND | 1Female 3 POS wire housing

I6

CONN TERM
FEMALE
24-30AWG GOLD

DigiKey
WM2513-ND | 3

Female 24-30
Gauge Crimp
Connector


I7 CONN TERM MALE
22-24AWG GOLD

DigiKey
WM2515-ND | 12

Male 24-30
Gauge Crimp
Connector

I8

Extreme-Temperature
Teflon® PTFE Semi-Clear Tubing

McMaster-Carr
5239K12 | 1 | Plastic Tubing

I9

Carbon Fiber Sleeve
Outer Bracket
(No Temp)

3D Printer
N/A | 1 | Sleeve Bracket


I10

Carbon Fiber Sleeve
Outer Bracket
(Temp)

3D Printer
N/A | 1 | Sleeve Bracket

I11 Carbon Fiber Sleeve
Inner Bracket

3D Printer
N/A | 1 | Sleeve Bracket
I12 | Needle Holder | 3D Printer
N/A | 1

Needle Guide for
Stabilized X-Carriage

J1 | 3 inch Aluminum
Channel | ServoCity 585442 | 1 | Gear Box
J2 | 55:1 Gear Ratio
55 Teeth Worm Gear SDP-SI S1C83Z-P048B055S 1 | Gear Box
J3 | Center Hole Adaptors
(4 pack) | ServoCity 633138 | 4 | Gear Box

J4

1/8 inch ID x 3/8 inch
OD
Ball Bearing (2 pack)
ServoCity 535206 | 4 | Gear Box

J5

48 D.P. 24 Teeth
20° Pressure Angle
AGMA Q10 Quality
With ( Hub / S.S.)
2024 Aluminum Alloy
Gear
SDP-SI S1063Z-048A024 1 | Gear Box

J6

48 D.P. 48 Teeth
20° Pressure Angle
AGMA Q10 Quality
With ( Hub / S.S.)
303 Stainless Steel
Gear
SDP-SI S1063Z-048S048 1 | Gear Box

J7

.12470" (+.000/-.0002)
Dia. 2.375" Long
303 Stainless Steel
Shaft
SDP-SI A 7X 1-04023 | 2 | Gear Box

J8

0.1248" Bore 0.3125"
O.D. 0.18" Wide
303 Stainless Steel
Collar Style
SDP-SI S5000Y-12510 | 1 | Gear Box

J9

0.125" I.D. 0.1875"
O.D. 0.016" Thick
Shaft Spacer
SDP-SI A 7X 8-C04016 | 3 | Gear Box

J10

0.125" I.D. 0.1875"
O.D. 0.031"
Thick Shaft Spacer
SDP-SI A 7X 8-C04031 | 1 | Gear Box

J11

32 DP 16 Teeth
20° Pressure Angle
Acetal / Brass Insert
Spur Gear
SDP-SI A 1T 2-Y32016 | 1 | Gear Box


J12 90 Degree Quad Hub
Mount B | ServoCity 545424 | 1 | Gear Box
J13 Beam Bracket T (Pair) | ServoCity 585656 | 2 | Gear Box


J14 | Beam Attachment
Block B (4 pack) | ServoCity 585600 | 4 | Gear Box
J15 | 1 inch Bore Tube
Clamp A | ServoCity 585434 | 2 | Gear Box

J16 90 Degree Quad Hub
Mount C | ServoCity 545360 | 1 | Gear Box

J17 Attachment Blocks (12
pack) | ServoCity 585400 | 1 | Extruder Arm


J18 | 1.54 inch Aluminum
Beam (2 pack) | ServoCity 585404 | 2 | Extruder Arm
J19 | Beam Crossover
Adaptor A | ServoCity 585490 | 1 | Extruder Arm
J20 Beam Bracket F (Pair) | ServoCity 585612 | 2 | Extruder Arm

J21 | Syringe Plunger | N/A | 1 | Extruder Arm
J22 | 6.16 inch Aluminum
Beam (2 pack) | ServoCity 585416 | 1 | Extruder Arm
J23 32P Beam Gear Rack | ServoCity 615410 | 1 | Extruder Arm
J24 | Syringe Body | N/A | 1 | Extruder Arm

J25 Stepper Motor Mount
(NEMA 17)

ServoCity
555152 | 1 | Motor Mount

J26

3/16 inch to 5mm
Set Screw Shaft
Coupler

ServoCity
625176 | 1 | Motor Mount


J27 3/16 inch x 1 inch Precision Shaft ServoCity
634136 | 1 | Motor Mount

J28

48DP/1 Lead/.33PD
20° Pressure Angle
Stainless Steel Worm

SDP-SI
S1D94Z-P048SS | 1 | Motor Mount


A4 | M5 x 10 Bolt,
SHCS Black-Oxide

McMaster-Carr
91290A115 | 1 | Motor Mount
A5 | M5 Washer,
Steel, Zinc Plated

McMaster-Carr
91166A240 | 1 | Motor Mount


D10

Nema 17 Stepper
Motor
2 A 45 Ncm (64oz.in)

Amazon
17HS16-2004S1 | 1 | Motor Mount

H4

6-32x .750 inch
Aluminum Standoffs
(Round)

ServoCity
534-3488 | 4 | Motor Mount

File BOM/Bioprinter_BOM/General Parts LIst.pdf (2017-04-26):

1

### Steve Lammers

From: | Jim Velasquez <jim.velasquez@tinkermill.org>
Sent: | Friday, December 04, 2015 9:06 AM
To: | Lammers, Steven
Cc: | Harn, Casey; Rich Ackley; Wagner, Jennifer
Subject: | Re: Bioprinter

Here are more material sourcing notes from my build log of Rich's printer:

Again, all are qty needed per printer

ACME Nuts QTY 2ea. http://www.mcmaster.com/#95155a111/=zjxac0

Leadscrews qty 1 ea. https://www.mscdirect.com/product/details/04354635

8mm rod (5/16" drill rod) qty 2 ea https://www.fastenal.com/products/details/47768

Amazon.com parts (prime only, fast delivery)

Power supply:

http://www.amazon.com/gp/product/B00KXV4WH8?psc=1&redirect=true&ref_=oh_aui_detailpage_o00_s02

GT2 timing belt and pulleys

http://www.amazon.com/gp/product/B00THZJNTI?refRID=32517S1TZQSCBGJ8AKWA&ref_=pd_bia_nav_t_1

Linear Bearing:

http://www.amazon.com/gp/product/B00IK4NLCC?psc=1&redirect=true&ref_=oh_aui_detailpage_o02_s00

Arduino mega2560

http://www.amazon.com/SunFounder-ATmega2560-16AU-Board-compatible-Arduino/dp/B00D9NA4CY/ref=sr_1_5?ie=UTF8&qid=1449243226&sr=8-5&keywords=arduino+2560&refinements=p_85%3A2470955011

RAMPS electronics daughterboard

http://www.amazon.com/gp/product/B00MQH49ZC?psc=1&redirect=true&ref_=oh_aui_detailpage_o00_s00

Stepstick A4988 stepper driver set

http://www.amazon.com/gp/product/B00MQR93QC?psc=1&redirect=true&ref_=oh_aui_detailpage_o01_s00

2

Stepper motor set for Mendel

http://www.amazon.com/gp/product/B00QEXSCE8?psc=1&redirect=true&ref_=oh_aui_detailpage_o03_s00

Heated bed [do you really need a heated bed?]

http://www.amazon.com/gp/product/B00EZKEGG0?psc=1&redirect=true&ref_=oh_aui_detailpage_o00_s02

http://www.amazon.com/gp/product/B00GD471PO?psc=1&redirect=true&ref_=od_aui_detailpages02

NOTE: The following are not prime eligible, will need expedited shipping for fast delivery

End stop kit

http://www.amazon.com/gp/product/B014Y0VGOU?psc=1&redirect=true&ref_=oh_aui_detailpage_o04_s05

Mendel / Reprap basic wiring kit for RAMPS

http://www.amazon.com/gp/product/B00SCJNP7G?psc=1&redirect=true&ref_=oh_aui_detailpage_o08_s00

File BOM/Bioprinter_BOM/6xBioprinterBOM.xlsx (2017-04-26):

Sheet: 6x Bioprinters
 |  |  |  |  |  | Multiplier = | 6
Mendel Frame BOM
Vendor | Part Number | Quantity | Description | Cost Per Pkg | Total Cost | Pkg pcs | Mult-x Quantity | Round Up | Total Cost | Website
Misumi | HNKK5-5 | 100 | Nuts for Aluminum Frame | $15.26 | $15.26 | 100.00 | 6 | 6 | $91.56 | http://us.misumi-ec.com
Misumi | HFS5-2020-265-TPW | 4 | Aluminum Extrusion - 265mmv - Tapped Ends | $6.63 | $26.52 | 1.00 | 24 | 24 | $159.12 | http://us.misumi-ec.com
Misumi | HFS5-2020-300-TPW | 4 | Aluminum Extrusion - 300mm - Tapped Ends | $5.31 | $21.24 | 1.00 | 24 | 24 | $127.44 | http://us.misumi-ec.com
Misumi | HFS5-2020-385-TPW-AH70-BH315 | 2 | Aluminum Extrusion - 385mm - Tapped Ends, Horz Drilled Holes | $8.79 | $17.58 | 1.00 | 12 | 12 | $105.48 | http://us.misumi-ec.com
Misumi | HFS5-2020-380-TPW | 4 | Aluminum Extrusion - 380mm - Tapped Ends | $5.76 | $23.04 | 1.00 | 24 | 24 | $138.24 | http://us.misumi-ec.com
McMaster | 98935A410 | 1 | Leadscrews - 3/8-12 Thread, 6 Ft. Long, Left Hand, Acme Threaded Rod | $13.66 | $13.66 | 1.00 | 6 | 6 | $81.96 | https://www.mscdirect.com/product/details/04354635
McMaster | 88625K67 | 2 | 8mm rod (5/16" drill rod) 36"O1 Tool Steel | $5.70 | $11.40 | 1.00 | 12 | 12 | $68.40 | https://www.fastenal.com/products/details/47768
Amazon | N/A | 2 | 2 x Aluminum GT2 16T Pulley and 2M Belt for RepRap 3D printer Prusa i3 | $14.95 | $14.95 | 2.00 | 6 | 6 | $89.70 | http://www.amazon.com/gp/product/B00THZJNTI?refRID=32517S1TZQSCBGJ8AKWA&ref_=pd_bia_nav_t_1
Amazon | N/A | 1 | 12x LM8UU Linear Bearing | $24.95 | $24.95 | 1.00 | 6 | 6 | $149.70 | http://www.amazon.com/gp/product/B00IK4NLCC?psc=1&redirect=true&ref_=oh_aui_detailpage_o02_s00
Amazon | N/A | 4 | 608ZZ Bearings | $17.07 | $17.07 | 30.00 | 0.8 | 1 | $17.07 | http://www.amazon.com/Bearing-Shielded-Greased-Miniature-Bearings/dp/B002BBD6X4?dpID=51iStG7O5sL&dpSrc=sims&preST=_AC_UL160_SR160%2C160_
Total Cost |  |  |  |  |  |  |  |  | $1028.67
Mendel Hardware BOM
Vendor | Part Number | Quantity | Description | Cost Per Pkg | Total Cost | Pkg pcs | Mult-x Quantity | Round Up | Total Cost | Website
McMaster-Carr | 91290A224 | 86 | M5 x 10 Bolt, SHCS Black-Oxide | $9.55 | $9.55 | 100.00 | 5.16 | 6 | $57.30
McMaster-Carr | 91166A240 | 84 | M5 Washer | $2.19 | $2.19 | 100.00 | 5.04 | 6 | $13.14
McMaster-Carr | 91166A210 | 73 | M3 Washer, Steel, Zinc Plated | $1.61 | $1.61 | 100.00 | 4.38 | 5 | $8.05
McMaster-Carr | 90576A102 | 42 | M3 Nyloc Nut | $3.27 | $3.27 | 100.00 | 2.52 | 3 | $9.81
McMaster-Carr | 91290A115 | 30 | M3 x 10 Bolt, SHCS Black-Oxide | $6.81 | $6.81 | 100.00 | 1.8 | 2 | $13.62
McMaster-Carr | 91290A230 | 28 | M5 x 14 Bolt, SHCS Black-Oxide | $11.70 | $11.70 | 100.00 | 1.68 | 2 | $23.40
McMaster-Carr | 91166A270 | 22 | M8 Washer | $3.23 | $3.23 | 100.00 | 1.32 | 2 | $6.46
McMaster-Carr | 91290A120 | 22 | M3 x 16 Bolt, SHCS Black-Oxide | $8.20 | $8.20 | 100.00 | 1.32 | 2 | $16.40
McMaster-Carr | 94180A331 | 20 | Threaded Insert 3mm | $12.30 | $12.30 | 100.00 | 1.2 | 2 | $24.60
McMaster-Carr | 90591A146 | 18 | M5 Nut | $2.08 | $2.08 | 100.00 | 1.08 | 2 | $4.16
McMaster-Carr | 91290A117 | 16 | M3 x 12 Bolt, SHCS Black-Oxide | $7.75 | $7.75 | 100.00 | 0.96 | 1 | $7.75
McMaster-Carr | 91290A123 | 14 | M3 x 20 Bolt, SHCS Black-Oxide | $9.70 | $9.70 | 100.00 | 0.84 | 1 | $9.70
McMaster-Carr | 91166A230 | 13 | M4 Washer | $1.96 | $1.96 | 100.00 | 0.78 | 1 | $1.96
McMaster-Carr | 91280A140 | 9 | M4 x 20 Bolt, Hex Head | $7.19 | $7.19 | 100.00 | 0.54 | 1 | $7.19
McMaster-Carr | 90591A141 | 9 | M4 Nut,Zinc-Plated Steel | $1.39 | $1.39 | 100.00 | 0.54 | 1 | $1.39
McMaster-Carr | 91239A232 | 7 | M5 x 16 Bolt, BHCS Black-Oxide | $8.82 | $8.82 | 100.00 | 0.42 | 1 | $8.82
McMaster-Carr | 94300A310 | 7 | M4 Wing Nut | $8.36 | $8.36 | 50.00 | 0.84 | 1 | $8.36
McMaster-Carr | 90592A009 | 6 | M3 Nut | $1.04 | $1.04 | 100.00 | 0.36 | 1 | $1.04
McMaster-Carr | 91290A019 | 6 | M2 Socket Head Cap Screw Thread,12mm | $11.29 | $11.29 | 100.00 | 0.36 | 1 | $11.29
McMaster-Carr | 90591A111 | 6 | M2Hex Nut, Zinc-Plated .4mm pitch, | $1.39 | $1.39 | 100.00 | 0.36 | 1 | $1.39
McMaster-Carr | 91166A180 | 6 | M2 Steel Flat Washer, zinc-plated | $1.43 | $1.43 | 100.00 | 0.36 | 1 | $1.43
McMaster-Carr | 90576A104 | 5 | M5 Nut Nyloc | $4.27 | $4.27 | 100.00 | 0.3 | 1 | $4.27
McMaster-Carr | 7130K52 | 5 | Cable Ties 4"L, 7/8" Bundle Dia | $2.43 | $2.43 | 100.00 | 0.3 | 1 | $2.43
McMaster-Carr | 94669A146 | 4 | Standoff, Aluminum for M5, OD 10mm, 30mm Long | $1.27 | $5.08 | 1.00 | 24 | 24 | $30.48
McMaster-Carr | 91239A244 | 4 | M5 x 45 Bolt, BHCS Black-Oxide | $4.72 | $4.72 | 10.00 | 2.4 | 3 | $14.16
McMaster-Carr | 91239A224 | 4 | M5 x 10 Bolt, BHCS Black-Oxide | $7.93 | $7.93 | 100.00 | 0.24 | 1 | $7.93 | Button Heads for T-channel
McMaster-Carr | 91290A168 | 4 | M4 x 20 Bolt, SHCS Black-Oxide | $9.70 | $9.70 | 100.00 | 0.24 | 1 | $9.70
McMaster-Carr | 91290A125 | 4 | M3 x 25 Bolt, SHCS Black-Oxide | $11.92 | $11.92 | 100.00 | 0.24 | 1 | $11.92
McMaster-Carr | 91290A110 | 4 | M3 x 5 Bolt, SHCS Black-Oxide | $7.97 | $7.97 | 100.00 | 0.24 | 1 | $7.97
McMaster-Carr | 90576A117 | 3 | M8 Nut Nyloc | $9.77 | $9.77 | 100.00 | 0.18 | 1 | $9.77
McMaster-Carr | 91175A620 | 3 | Thumb Screw Knob for M4 SHCS | $9.21 | $9.21 | 50.00 | 0.36 | 1 | $9.21
McMaster-Carr | 9681K15 | 2 | Wire Ferrules 24-20 AWG | $6.32 | $6.32 | 100.00 | 0.12 | 1 | $6.32
McMaster-Carr | 95155A111 | 2 | 3/8-12 ACME Hex Nut | $5.12 | $10.24 | 1.00 | 12 | 12 | $61.44
McMaster-Carr | 91290A187 | 2 | M4 x 55 hex head bolt | $7.67 | $7.67 | 25.00 | 0.48 | 1 | $7.67
McMaster-Carr | 91116A130 | 2 | M4 Washer, Large Diameter | $3.87 | $3.87 | 100.00 | 0.12 | 1 | $3.87
McMaster-Carr | 91290A438 | 1 | M8 x 35 Bolt, SHCS Black-Oxide | $9.19 | $9.19 | 50.00 | 0.12 | 1 | $9.19
McMaster-Carr | 91290A434 | 1 | M8 x 30 Bolt, SHCS Black-Oxide | $8.46 | $8.46 | 50.00 | 0.12 | 1 | $8.46
McMaster-Carr | 91280A548 | 1 | M8 x 55 Hex Head Bolt | $8.61 | $8.61 | 25.00 | 0.24 | 1 | $8.61
McMaster-Carr | 91390A100 | 1 | M3 Set Screw (Grub Screw) | $4.78 | $4.78 | 100.00 | 0.06 | 1 | $4.78
McMaster-Carr | 90576A103 | 1 | Nut, Nylock,M4-0.7,Steel,ZN | $3.91 | $3.91 | 100.00 | 0.06 | 1 | $3.91
McMaster-Carr | 91175A066 | 1 | Metric Press-Fit Plastic Thumb Screw Head, Knurled, Black, Fits M8 | $7.92 | $7.92 | 25.00 | 0.24 | 1 | $7.92
McMaster-Carr | 92185A144 | 2 | 6-32 SS Socket Head Cap Screws - 1/4" | $2.75 | $2.75 | 25.00 | - | 2 | $5.50
McMaster-Carr | 92185A145 | 2 | 6-32 SS Socket Head Cap Screws - 5/16" | $2.65 | $2.65 | 25.00 | - | 2 | $5.30
McMaster-Carr | 92185A147 | 2 | 6-32 SS Socket Head Cap Screws - 3/8" | $2.56 | $2.56 | 25.00 | - | 2 | $5.12
McMaster-Carr | 92185A163 | 2 | 6-32 SS Socket Head Cap Screws - 7/16" | $4.74 | $4.74 | 25.00 | - | 2 | $9.48
McMaster-Carr | 92185A148 | 2 | 6-32 SS Socket Head Cap Screws - 1/2" | $2.74 | $2.74 | 25.00 | - | 2 | $5.48
McMaster-Carr | 9948T22 | 3 | 22 Ga Multi Color hookup Wire Kit | $65.75 | $65.75 | 26.00 | - | 1 | $65.75
Total Cost |  |  |  |  |  |  |  |  | $563.90
Mendel Electrical BOM
Vendor | Part Number | Quantity | Description | Cost Per Unit | Total Cost | Pkg pcs | Mult-x Quantity | Round Up | Total Cost | Website
Amazon | N/A | 1 | 12V 30A DC Universal Regulated Switching Metal Case Power Supply Adaptor Transformer 360W | $25.27 | $25.27 | 1.00 | 6 | 6 | $151.62 | http://www.amazon.com/gp/product/B00KXV4WH8?psc=1&redirect=true&ref_=oh_aui_detailpage_o00_s02
Amazon | N/A | 1 | 14 AWG 3 Prong AC Power Cord, Pigtail (Open End), 15 Amp Max, 10 ft | $17.99 | $17.99 | 1.00 | 6 | 6 | $107.94 | http://www.amazon.com/Prong-Power-Cord-Pigtail-Open/dp/B00LDXXJ38
Amazon | N/A | 1 | Arduino MEGA2560 | $17.99 | $17.99 | 1.00 | 6 | 6 | $107.94 | http://www.amazon.com/SunFounder-ATmega2560-16AU-Board-compatible-Arduino/dp/B00D9NA4CY
Amazon | N/A | 1 | RAMPS V1.4 Electronics Board | $10.09 | $10.09 | 1.00 | 6 | 6 | $60.54 | http://www.amazon.com/Hobbypower-Printer-Controller-REPRAP-Arduino/dp/B00MQH49ZC?rps=1
Amazon | N/A | 1 | 5x A4988 stepper Motor Driver | $8.49 | $8.49 | 1.00 | 6 | 6 | $50.94 | http://www.amazon.com/gp/product/B00MQR93QC?psc=1&redirect=true&ref_=oh_aui_detailpage_o01_s00
Amazon | N/A | 1 | 5x Stepper Motor Set, 2A, 40mm body, NEMA17, 64 oz.in. | $62.00 | $62.00 | 1.00 | 6 | 6 | $372.00 | http://www.amazon.com/gp/product/B00QEXSCE8?psc=1&redirect=true&ref_=oh_aui_detailpage_o03_s00
Amazon | N/A | 1 | 5x Mechanical Endstops/Limit Switch | $12.99 | $12.99 | 1.00 | 6 | 6 | $77.94 | http://www.amazon.com/gp/product/B014Y0VGOU?psc=1&redirect=true&ref_=oh_aui_detailpage_o08_s00
Amazon | N/A | 1 | Basic Wiring Kit for RAMPS | $7.59 | $7.59 | 1.00 | 6 | 6 | $45.54 | http://www.amazon.com/gp/product/B00SCJNP7G?psc=1&redirect=true&ref_=oh_aui_detailpage_o08_s00
Digikey | 259-1566-ND | 1 | 12VDC Fan | $3.87 | $3.87 | 1.00 | 6 | 6 | $23.22 | http://www.digikey.com/product-search/en?vendor=0&keywords=ME40101V1-000U-A99
Amazon |  | 1 | Epoxy | $27.20 | $27.20 | 1.00 | 1 | 1 | $27.20
Total Cost |  |  |  |  |  |  |  |  | $1024.88
Syringe Extruder BOM
Vendor | Part Number | Quantity | Description | Cost per unit | Total Cost | Pkg pcs | Mult-x Quantity | Round Up | Total Cost
Rockwest | BR-C-050 | 1.5 | Dry Braided Sleeve - Carbon Fiber - 0.5" | $1.85 | $2.78 | 1.00 | 9 | 9 | $16.65
Digikey | FQP30N06L-ND | 4 | MOSFET | $0.90 | $3.59 | 1.00 | 24 | 24 | $21.55
Digikey | 438-1046-ND | 1 | Breadboard | $12.44 | $12.44 | 1.00 | 6 | 6 | $74.64
Digikey | DS18B20+-ND | 4 | TempSensor | $2.68 | $10.71 | 1.00 | 24 | 24 | $64.27
Digikey | 1050-1041-ND | 1 | Arduino_UNO | $21.54 | $21.54 | 1.00 | 6 | 6 | $129.24
Digikey | T1171-P5RP-ND | 1 | Power_Adapter_5V_3.6A | $15.93 | $15.93 | 1.00 | 6 | 6 | $95.58
Digikey | 839-1219-ND | 1 | Barrel_Jack_to_Gator | $7.31 | $7.31 | 1.00 | 6 | 6 | $43.86
Digikey | WM2534-ND | 4 | 3-POS Molex Female | $0.56 | $2.22 | 1.00 | 24 | 24 | $13.32
Digikey | WM2516-ND | 12 | Molex Connector Pin Crimp Gold 24-30AWG | $0.29 | $3.43 | 1.00 | 72 | 72 | $20.59 | Could also use WM2565-CT @ 0.13ea
Digikey | WM2901-ND | 4 | 3-POS Molex Male | $0.19 | $0.74 | 1.00 | 24 | 24 | $4.46
Digikey | WM2513-ND | 12 | Molex Connector Socket Crimp Gold 24-30AWG | $0.12 | $1.42 | 1.00 | 72 | 72 | $8.50 | Could also use WM2562-CT @ 0.12ea
Digikey | WM2533-ND | 4 | 2-POS Molex Female | $0.53 | $2.12 | 1.00 | 24 | 24 | $12.74
Digikey | WM2515CT-ND | 8 | Molex Connector Pin Crimp Gold 22-24AWG | $0.20 | $1.61 | 1.00 | 48 | 48 | $9.66 | Could also use WM2517CT-ND @ 0.15ea
Digikey | WM2900-ND | 4 | 2-POS Molex Male | $0.22 | $0.88 | 1.00 | 24 | 24 | $5.30
Digikey | WM2512-ND | 8 | Molex Connector Socket Crimp Gold 22-24AWG | $0.15 | $1.18 | 1.00 | 48 | 48 | $7.07 | Could also use WM2510CT-ND @ 0.13ea
Sparkfun | COM-11288 | 1 | Heating Pad - 5x10cm | $3.95 | $3.95 | 1.00 | 6 | 6 | $23.70
Sparkfun | PRT-10811 | 1 | DC Barrel Jack Adapter - Breadboard Compatible | $0.95 | $0.95 | 1.00 | 6 | 6 | $5.70
SDP-SI | A 7X 1-06012 | 1 | .18720" (+.000/-.0002) Dia. 1.25" Long 303 Stainless Steel Shaft | $2.46 | $2.46 | 1.00 | 6 | 6 | $14.76
SDP-SI | A 7X 1-04023 | 2 | .12470" (+.000/-.0002) Dia. 2.375" Long 303 Stainless Steel Shaft | $2.46 | $4.92 | 1.00 | 12 | 12 | $29.52
SDP-SI | A 7X 8-C04031 | 1 | 0.125" I.D. 0.1875" O.D. 0.031" Thick Shaft Spacer | $1.10 | $1.10 | 1.00 | 6 | 6 | $6.60
SDP-SI | A 7X 8-C04016 | 3 | 0.125" I.D. 0.1875" O.D. 0.016" Thick Shaft Spacer | $1.01 | $3.03 | 1.00 | 18 | 18 | $18.18
SDP-SI | S5000Y-12510 | 1 | 0.1248" Bore 0.3125" O.D. 0.18" Wide 303 Stainless Steel Collar Style | $3.56 | $3.56 | 1.00 | 6 | 6 | $21.36
SDP-SI | A 1T 2-Y32016 | 1 | 32 DP 16 Teeth 20Â° Pressure Angle Acetal / Brass insert spur Gear | $5.10 | $5.10 | 1.00 | 6 | 6 | $30.60
SDP-SI | S1C83Z-P048B055S | 1 | 55:1 Gear Ratio 55 Teeth Worm Gear | $36.91 | $36.91 | 1.00 | 6 | 6 | $221.46
SDP-SI | S1D94Z-P048SS | 1 | 48DP/1 Lead/.33PD 20Â° Pressure Angle Stainless Steel Worm | $18.09 | $18.09 | 1.00 | 6 | 6 | $108.54
SDP-SI | S1063Z-048S024 | 1 | 48 D.P. 24 Teeth 20Â° Pressure Angle AGMA Q10 Quality With ( Hub / S.S.) 2024 Stainless Steel Gear. | $14.60 | $14.60 | 1.00 | 6 | 6 | $87.60
SDP-SI | S1063Z-048S048 | 1 | 48 D.P. 48 Teeth 20Â° Pressure Angle AGMA Q10 Quality With ( Hub / S.S.) 303 Stainless Steel Gear. | $18.57 | $18.57 | 1.00 | 6 | 6 | $111.42 | $650.04
Servocity | 585442 | 1 | 3.00 inch Aluminum Channel | $3.99 | $3.99 | 1.00 | 6 | 6 | $23.94
Servocity | 555152 | 1 | Stepper Motor Mount (NEMA 17) | $7.49 | $7.49 | 1.00 | 6 | 6 | $44.94
Servocity | 625176 | 1 | 3/16 inch to 5mm Set Screw Shaft Coupler | $4.99 | $4.99 | 1.00 | 6 | 6 | $29.94
Servocity | 634136 | 1 | 3/16 inch x1 inch Precision Shaft | $0.49 | $0.49 | 1.00 | 6 | 6 | $2.94
Servocity | 634138 | 1 | 3/16 inch x2 inch Precision Shaft | $0.69 | $0.69 | 1.00 | 6 | 6 | $4.14
Servocity | 633138 | 2 | Center Hole Adaptors (4 pack) | $1.99 | $3.98 | 1.00 | 12 | 12 | $23.88
Servocity | 535206 | 2 | 1/8 inch ID x 3/8 inch OD Ball Bearing (2 pack) | $1.99 | $3.98 | 1.00 | 12 | 12 | $23.88
Servocity | 545424 | 1 | 90 Degree Quad Hub Mount B | $4.99 | $4.99 | 1.00 | 6 | 6 | $29.94
Servocity | 585656 | 1 | Beam Bracket T (Pair) | $1.49 | $1.49 | 1.00 | 6 | 6 | $8.94
Servocity | 585600 | 1 | Beam Attachment Block B (4 pack) | $4.99 | $4.99 | 1.00 | 6 | 6 | $29.94
Servocity | 585416 | 1 | 6.16 inch Aluminum Beam (2 pack) | $5.49 | $5.49 | 1.00 | 6 | 6 | $32.94
Servocity | 615410 | 1 | 32P Beam Gear Rack | $5.99 | $5.99 | 1.00 | 6 | 6 | $35.94
Servocity | 585434 | 2 | 1 inch Bore Tube Clamp A | $5.99 | $11.98 | 1.00 | 12 | 12 | $71.88
Servocity | 585612 | 1 | Beam Bracket F (Pair) | $1.49 | $1.49 | 1.00 | 6 | 6 | $8.94
Servocity | 585404 | 1 | 1.54 inch Aluminum Beam (2 pack) | $2.39 | $2.39 | 1.00 | 6 | 6 | $14.34
Servocity | 585490 | 1 | Beam Crossover Adaptor A | $2.99 | $2.99 | 1.00 | 6 | 6 | $17.94
Servocity | 585400 | 1 | Attachment Blocks (12 pack) | $9.99 | $9.99 | 1.00 | 6 | 6 | $59.94
Servocity | 545360 | 1 | 90 Degree Quad Hub Mount C | $5.99 | $5.99 | 1.00 | 6 | 6 | $35.94
Servocity | 632146 | 1 | Actobotics Hardware Pack A | $39.99 | $39.99 | 1.00 | 2 | 2 | $79.98 | Don't need 1 ea
Servocity | 534-3488 | 4 | 6-32x .750 inch Aluminum Standoffs (Round) | $0.45 | $1.80 | 1.00 | 24 | 24 | $10.80 | ServoCity Total | $591.12 | Ordered | Shipping | 6.99 | Total | 598.11 | Invoice | ..\..\..\Class\Invoices\ServoCity_6x.pdf
Total Cost |  |  |  |  |  |  |  |  | $1798.00
Cooling System BOM
Vendor | Part Number | Quantity | Description | Cost per unit | Total Cost | Pkg pcs | Mult-x Quantity | Round Up | Total Cost
Digikey | FQP30N06L-ND | 2 | MOSFET | $0.90 | $1.80 | 1.00 | 12 | 12 | $10.78
Digikey | 1050-1041-ND | 1 | Arduino_UNO | $21.54 | $21.54 | 1.00 | 6 | 6 | $129.24
Digikey | ATS1758 | 1 | Heat Sink 60x60x25mm | $12.84 | $12.84 | 1.00 | 6 | 6 | $77.04
Digikey | 259-1317-ND | 1 | Squirrel Cage Blower(2-wire, 3-wire 603-1370-ND) | $8.64 | $8.64 | 1.00 | 6 | 6 | $51.84
Digikey | 3M12011-ND | 1 | Adhesive Heat Tape | $5.62 | $5.62 | 1.00 | 6 | 6 | $33.72
Amazon | N/A | 1 | Thermoelectric Cooler 40mmx40mm -TEC1-12706 | $5.99 | $5.99 | 1.00 | 6 | 6 | $35.94 | http://www.amazon.com/gp/product/B002UQQ3Q2?redirect=true
Amazon | N/A | 1 | Command Strips Refill Small 20-Strips - 4 pack | $19.99 | $19.99 | 1.00 | 1 | 1 | $19.99 | http://www.amazon.com/Command-Small-Refill-Strips-20-Strip/dp/B000FDLFBK
Total Cost |  |  |  |  |  |  |  |  | $358.55
Misc Electrical BOM
Vendor | Part Number | Quantity | Description | Cost per unit | Total Cost | Pkg pcs | Mult-x Quantity | Round Up | Total Cost
Sparkfun | ML8511 | 1 | UV Sensor Breakout Board | $12.95 | $12.95 | 1.00 | 1 | 1 | $12.95 | Don't need 1 ea
Digikey | ASW40-25-ND | 1 | Cable Wrap - 1/8" 25ft | $17.30 | $17.30 | 1.00 | 0 | 0 | $0.00 | Already Have
Digikey | ASW41-25-ND | 1 | Cable Wrap - 1/4" 25ft | $12.64 | $12.64 | 1.00 | 1 | 1 | $12.64 | Don't need 1 ea
Digikey | ASW43-25-ND | 1 | Cable Wrap - 1/2" 25ft | $23.46 | $23.46 | 1.00 | 1 | 1 | $23.46 | Don't need 1 ea
Digikey | Q2F1-KIT-ND | 1 | Heatshrink Kit | $22.20 | $22.20 | 1.00 | 1 | 1 | $22.20 | Don't need 1 ea | $894.92
Amazon |  | 1 | Joe Knows Electronics 33 Value 645 Piece Capacitor Kit | $19.99 | $19.99 | 1.00 | 1 | 1 | $19.99 | Don't need 1 ea
~~Amazon~~ |  | ~~1~~ | ~~Joe Knows Electronics Semiconductor Kit (320 Transistors & Diodes)~~ | ~~$29.99~~ | ~~$29.99~~ | ~~1.00~~ | ~~0~~ | ~~0~~ | ~~$0.00~~ | Already Have
Amazon |  | 1 | Joe Knows Electronics 1/4W 86 Value 860 Piece Resistor Kit | $17.99 | $17.99 | 1.00 | 1 | 1 | $17.99 | Don't need 1 ea
 |  |  |  |  | $0.00 | 1.00 | 0 | 0 | $0.00
 |  |  |  |  | $0.00 | 1.00 | 0 | 0 | $0.00
Total Cost |  |  |  |  |  |  |  |  | $109.23
Tools BOM
Vendor | Part Number | Quantity | Description | Cost per unit | Total Cost | Pkg pcs | Mult-x Quantity | Round Up | Total Cost
Amazon | N/A | 1 | Helping Hands | $6.31 | $6.31 | 1.00 | 4 | 4 | $25.24 | http://www.amazon.com/Helping-Hand-01902-with-Magnifier/dp/B000P42O3C?s=industrial
Amazon | N/A | 1 | Engineer PA-09 Micro Connector Crimpers | $38.40 | $38.40 | 1.00 | 4 | 4 | $153.60 | http://www.amazon.com/dp/B002AVVO7K?colid=3TC1Z36RD4QTY&coliid=I2LXQGH4SVIFVP
Amazon | N/A | 1 | Greenlee PA1118 GripP 20 Wire Stripper/Cutter, 30-20 AWG | $13.29 | $13.29 | 1.00 | 4 | 4 | $53.16 | http://www.amazon.com/dp/B0006BHHDQ?colid=3TC1Z36RD4QTY&coliid=I1ARHJXW0B512T
Amazon | N/A | 1 | Sm Wire Cutters | $4.37 | $4.37 | 1.00 | 4 | 4 | $17.48 | http://www.amazon.com/gp/product/B00FZPDG1K/ref=pd_luc_rh_bxgy_01_02_t_img_lh?ie=UTF8&psc=1
SDP-SI | A 4T15-094 | 1 | Hex Wrench Small | $0.58 | $0.58 | 1.00 | 4 | 4 | $2.32
SDP-SI | A 4T15-078 | 1 | Hex Wrench Small | $0.54 | $0.54 | 1.00 | 4 | 4 | $2.16
SDP-SI | A 4T15-062 | 1 | Hex Wrench Small | $0.52 | $0.52 | 1.00 | 4 | 4 | $2.08
SDP-SI | A 4T15-050 | 1 | Hex Wrench Small | $0.52 | $0.52 | 1.00 | 4 | 4 | $2.08
SDP-SI | A 4T15-035 | 1 | Hex Wrench Small | $0.61 | $0.61 | 1.00 | 4 | 4 | $2.44
SDP-SI | A 4T15-028 | 1 | Hex Wrench Small | $0.98 | $0.98 | 1.00 | 4 | 4 | $3.92 | $15.00 | $665.04
~~Digikey~~ | ~~8331S-15G~~ | ~~1~~ | ~~Conductive Epoxy 10min work time ~~ | ~~$49.61~~ | $49.61 | 1.00 | 0 | 0 | $0.00 | Already Have
Amazon | N/A | 1 | Soldering Iron - Weller WLC100 | $39.99 | $39.99 | 1.00 | 4 | 4 | $159.96 | http://www.amazon.com/Weller-WLC100-40-Watt-Soldering-Station/dp/B000AS28UC
Amazon |  | 1 | Lead Free Rosin Core Solder | $19.95 | $19.95 | 1.00 | 2 | 2 | $39.90 | http://www.amazon.com/Tenma-21-1046-Lead-Rosin-Solder/dp/B001DPVT1A
Sparkfun | TOL-10706 | 1 | Hot Air Rework Station | $114.95 | $114.95 | 1.00 | 2 | 2 | $229.90 | https://www.sparkfun.com/products/10706
Amazon | N/A | 1 | Hakko 599B-02 Solder Tip Cleaning Wire and Holder | $8.94 | $8.94 | 1.00 | 4 | 4 | $35.76 | http://www.amazon.com/gp/product/B00FZPGDLA?psc=1&redirect=true&ref_=oh_aui_search_detailpage
Amazon | N/A | 1 | Thermaltronics Tip Tinner | $7.95 | $7.95 | 1.00 | 4 | 4 | $31.80 | http://www.amazon.com/dp/B00NS4J6BY?psc=1
 |  |  | Drill
 |  |  | Various Drill bit sizes
 |  |  | Level
 |  |  | Xacto knife
 |  |  | dremel
 |  |  | super glue medium thick
 |  |  | Caliper (metric)
 |  |  | Voltmeter/DMM
 |  |  | Torque wrench
 |  | 4 | Wrench set |  | $0.00 | 1.00 | 4 | 4 | $0.00
 |  | 4 | Allen Keys |  | $0.00 | 1.00 | 4 | 4 | $0.00
Amazon | N/A | 1 | TEKTON 6655 Needle File Set, 10-Piece | $6.57 | $6.57 | 1.00 | 4 | 4 | $26.28 | http://www.amazon.com/TEKTON-6655-Needle-File-10-Piece/dp/B000NPUKYS?dpID=412lincr%2B5L&dpSrc=sims&preST=_AC_UL160_SR160%2C160_
Amazon | N/A | 1 | Shugru - 8 Pack | $22.00 | $22.00 | 1.00 | 2 | 2 | $44.00 | http://www.amazon.com/dp/B00EU7DBNM?colid=3TC1Z36RD4QTY&coliid=I1GUSCSW80A32Y
Total Cost |  |  |  |  |  |  |  |  | $832.08 | $786.11
Grand Total Cost - 6x Bioprinters with 1x extruder each |  |  |  |  |  |  |  |  | $5715.30
 |  |  |  |  |  |  |  |  |  | $272.25
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

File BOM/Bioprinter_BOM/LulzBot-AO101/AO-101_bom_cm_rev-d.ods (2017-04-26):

Item | Part Number | Qty | UOM | Rev | Description | Vendor | Vendor Part Number
1 | ALE-0000001 | 1 | ea | A | Assy, Budaschnozzle,Wired for Assembly
2 | ALE-0000014 | 73 | ea |  | M3 Washer, Steel, Zinc Plated | McMaster-Carr Supply Company | 91166A210
3 | ALE-0000015 | 2 | ea |  | Wire Ferrules 24-20 AWG | McMaster-Carr Supply Company | 9681K15
4 | ALE-0000022 | 1 | ea |  | 100k Honeywell Axial Thermistor | Honeywell | 135-104LAG-J01
5 | ALE-0000028 | 30 | ea |  | Female connector pins, 22-24 AWG | Molex Inc. | 16-02-0102
6 | ALE-0000034 | 2 | ea |  | Lower Vertex, Left | Aleph Objects | ALE-0000034
7 | ALE-0000035 | 4 | ea |  | Lower Vertex Middle | Aleph Objects | ALE-0000035
8 | ALE-0000036 | 2 | ea |  | Z Upper Idler | Aleph Objects | ALE-0000036
9 | ALE-0000037 | 2 | ea |  | Z Lower Motor Mount | Aleph Objects | ALE-0000037
10 | ALE-0000038 | 2 | ea |  | Y Rod Mount | Aleph Objects | ALE-0000038
11 | ALE-0000039 | 8 | ea |  | Z Clamp | Aleph Objects | ALE-0000039
12 | ALE-0000243 | 1 | EA |  | Y Motor Mount - AO-101 | Aleph Objects | ALE-0000243
13 | ALE-0000244 | 1 | EA |  | Y Idler Mount - Tensioner | Aleph Objects | ALE-0000244
14 | ALE-0000042 | 3 | EA |  | Top Vertex, Mini 45 | Aleph Objects | ALE-0000042
15 | ALE-0000043 | 4 | ea |  | Belt Clamp | Aleph Objects | ALE-0000043
16 | ALE-0000046 | 4 | ea |  | Aluminum Extrusion - 5 Series, 380mm | Fiero Fluid Power, Inc | HFS5-2020-420
 |  |  |  |  |  | Misumi | HFS5-2020-420
17 | ALE-0000047 | 2 | ea |  | Aluminum Extrusion - 5 Series, 385mm, tapped on both ends, 5mm hole drilled at 70mm from ends | Fiero Fluid Power, Inc | HFS5-2020-420-TPW
 |  |  |  |  |  | Misumi | HFS5-2020-420-TPW
18 | ALE-0000048 | 4 | ea |  | Aluminum Extrusion - 5 Series, 300mm, tapped on both ends | Fiero Fluid Power, Inc | HFS5-2020-340-TPW
 |  |  |  |  |  | Misumi | HFS5-2020-340-TPW
19 | ALE-0000049 | 4 | ea |  | Aluminum Extrusion - 5 Series, 265mm, tapped on both ends | Fiero Fluid Power, Inc | HFS5-2020-300-TPW
 |  |  |  |  |  | Misumi | HFS5-2020-300-TPW
20 | ALE-0000050 | 84 | ea |  | Pre-Assembly Square Nuts -For HFS5 | Misumi | HNKK5-5
21 | ALE-0000051 | 2 | ea | C | 8mm Smooth Rod x 375mm | Datum Machining, Inc. | ALE-0000051
22 | ALE-0000238 | 1 | EA | C | Bed Plate, AO-101 | EPOCS Manufacturing Inc. | ALE-0000238
23 | ALE-0000053 | 1 | ea | IR | Y Axix Plate | EPOCS Manufacturing Inc. | ALE-0000053
24 | ALE-0000054 | 5 | ea |  | Nema 17 Bipolar | Soyo | SY42STH47-1504A
25 | ALE-0000055 | 5 | ea |  | 4 pin connector housing | Molex Inc. | 50-57-9004
26 | ALE-0000056 | 9 | ea |  | 608ZZ Bearing | VXB.com | 100 Skate
27 | ALE-0000057 | 4 | ea |  | Standoff, Aluminum for M5, OD 10mm, 30mm Long | McMaster-Carr Supply Company | 94669A146
28 | ALE-0000058 | 18 | ea |  | M5 Nut | McMaster-Carr Supply Company | 90591A146
29 | ALE-0000059 | 5 | ea |  | M5 Nut Nyloc | McMaster-Carr Supply Company | 90576A104
30 | ALE-0000060 | 3 | ea |  | M8 Nut Nyloc | McMaster-Carr Supply Company | 90576A117
31 | ALE-0000061 | 84 | ea |  | M5 Washer | McMaster-Carr Supply Company | 91166A240
32 | ALE-0000062 | 22 | ea |  | M8 Washer | McMaster-Carr Supply Company | 91166A270
33 | ALE-0000063 | 30 | ea |  | M3 x 10 Bolt, SHCS Black-Oxide | McMaster-Carr Supply Company | 91290A115
34 | ALE-0000064 | 16 | ea |  | M3 x 12 Bolt, SHCS Black-Oxide | McMaster-Carr Supply Company | 91290A117
35 | ALE-0000065 | 86 | ea |  | M5 x 10 Bolt, SHCS Black-Oxide | McMaster-Carr Supply Company | 91290A224
36 | ALE-0000066 | 28 | ea |  | M5 x 14 Bolt, SHCS Black-Oxide | McMaster-Carr Supply Company | 91290A230
37 | ALE-0000067 | 7 | ea |  | M5 x 16 Bolt, BHCS Black-Oxide | McMaster-Carr Supply Company | 91239A232
38 | ALE-0000068 | 4 | ea |  | M5 x 45 Bolt, BHCS Black-Oxide | McMaster-Carr Supply Company | 91239A244
39 | ALE-0000069 | 1 | ea |  | M8 x 35 Bolt, SHCS Black-Oxide | McMaster-Carr Supply Company | 91290A438
40 | ALE-0000070 | 3 | ea |  | Thumb Screw Knob for M4 SHCS | McMaster-Carr Supply Company | 91175A620
41 | ALE-0000071 | 12 | ea |  | IGUS Bushing Pillow Block | Igus, Inc. | KSTM-08
42 | ALE-0000242 | 2 | EA |  | GT2 Timing Pulley, 5mm Bore Aluminum | B & B Manufacturing, Inc | 16-2P06M6CA5 5MM BORE ALUMINUM
43 | ALE-0000073 | 1 | ea |  | AO X-Axis Carriage Pillow | Aleph Objects | ALE-0000073
44 | ALE-0000074 | 1 | ea |  | AO X-Axis end Idler ACME | Aleph Objects | ALE-0000074
45 | ALE-0000075 | 1 | ea |  | AO X-Axis end motor mount ACME | Aleph Objects | ALE-0000075
46 | ALE-0000076 | 2 | ea |  | AO X-Axis end clamp ACME | Aleph Objects | ALE-0000076
47 | ALE-0000077 | 2 | EA |  | Beefy couplings ACME | Aleph Objects | ALE-0000077
48 | ALE-0000080 | 2 | EA |  | Belt, GT2 2mm, 1000mm, 6mm width | Stock Drive Products | A 6R51M582060
49 | ALE-0000081 | 2 | ea | A | 3/8-12 ACME Threaded Rod, 285mm,303 SS | Datum Machining, Inc. | ALE-0000081
50 | ALE-0000082 | 2 | ea |  | 3/8-12 ACME Hex Nut | McMaster-Carr Supply Company | 95155A111
51 | ALE-0000083 | 2 | ea | C | 8mm Smooth Rod x 410mm | Datum Machining, Inc. | ALE-0000083
52 | ALE-0000240 | 2 | EA | E | 8mm Smooth Rod x 310mm | Datum Machining, Inc. | ALE-0000240
53 | ALE-0000085 | 22 | ea |  | M3 x 16 Bolt, SHCS Black-Oxide | McMaster-Carr Supply Company | 91290A120
54 | ALE-0000086 | 4 | ea |  | M4 x 20 Bolt, SHCS Black-Oxide | McMaster-Carr Supply Company | 91290A168
55 | ALE-0000087 | 1 | ea |  | M8 x 30 Bolt, SHCS Black-Oxide | McMaster-Carr Supply Company | 91290A434
56 | ALE-0000088 | 6 | ea |  | M3 Nut | McMaster-Carr Supply Company | 90592A009
57 | ALE-0000089 | 42 | ea |  | M3 Nyloc Nut | McMaster-Carr Supply Company | 90576A102
58 | ALE-0000090 | 13 | ea |  | M4 Washer | McMaster-Carr Supply Company | 91166A230
59 | ALE-0000092 | 1 | ea | B | Heated Print Bed
60 | ALE-0000093 | 1 | EA |  | Borosilicate glass, 200mm x 214mm, 1/8" thick | Aleph Objects | ALE-0000093
61 | ALE-0000095 | 3.1 | ft |  | 16awg Wire, purple | Alpha Wire | 3057 VI005
 |  |  |  |  |  | Alpha Wire | 3057 VI001
62 | ALE-0000096 | 3.7 | ft |  | 24awg Wire, yellow | Alpha Wire | 3050 YL005
 |  |  |  |  |  | Alpha Wire | 3050 YL001
63 | ALE-0000097 | 4 | ea |  | Binder Clips | McMaster-Carr Supply Company | 12755T72
64 | ALE-0000098 | 4 | ea |  | Spring, Steel,0.18" OD,0.02" Wire Size,0.384" Compressed Length | Associated Spring | C0180-020-0750-M
65 | ALE-0000099 | 14 | ea |  | M3 x 20 Bolt, SHCS Black-Oxide | McMaster-Carr Supply Company | 91290A123
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

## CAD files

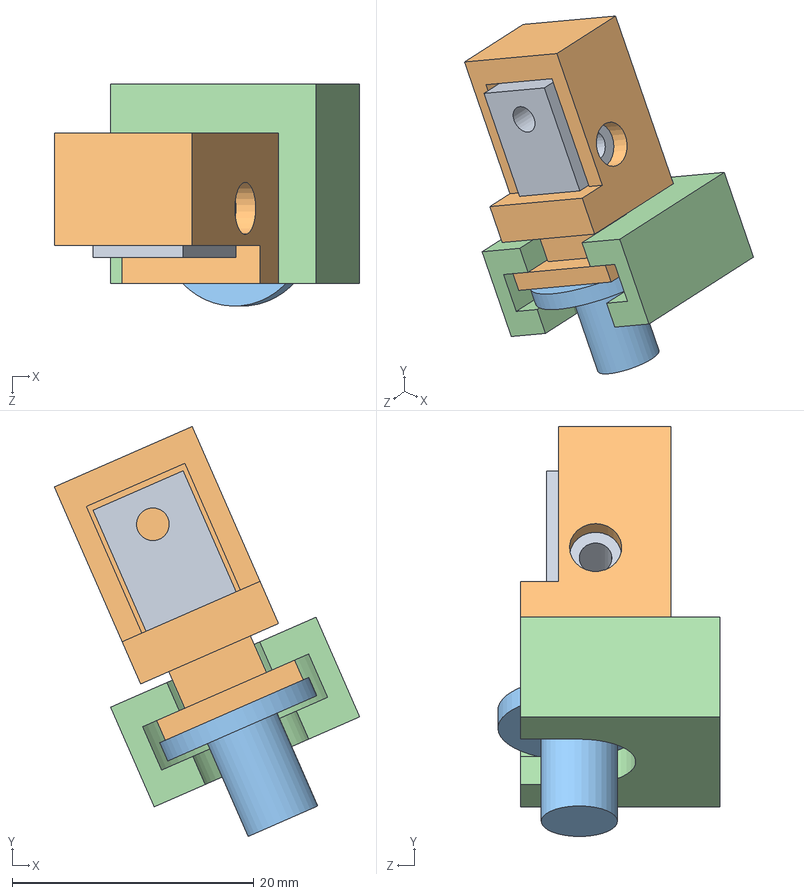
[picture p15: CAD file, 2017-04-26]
Hardware/Design/3mL_Syringe_Plunger_Attachment/3mL_Syringe_Plunger_Attachment.SLDASM
25.2 x 33.9 x 18.4 mm
Attachment_Blocks_585400_a
Part1^3mL_Syringe_Plunger_Attachment
Plunger_Flange
Part2^3mL_Syringe_Plunger_Attachment

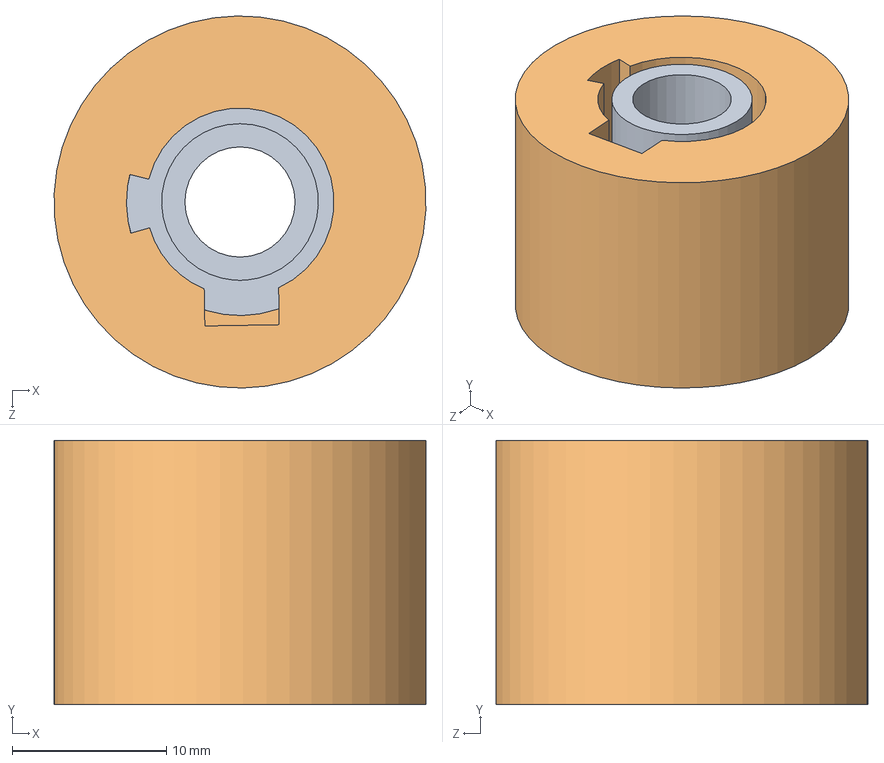
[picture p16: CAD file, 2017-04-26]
Hardware/Design/CarbonFiber_Sleeve_Brackets/CarbonFiber_Sleeve.SLDASM
24.1 x 17.1 x 24.1 mm
Inner
Outer2-Temp

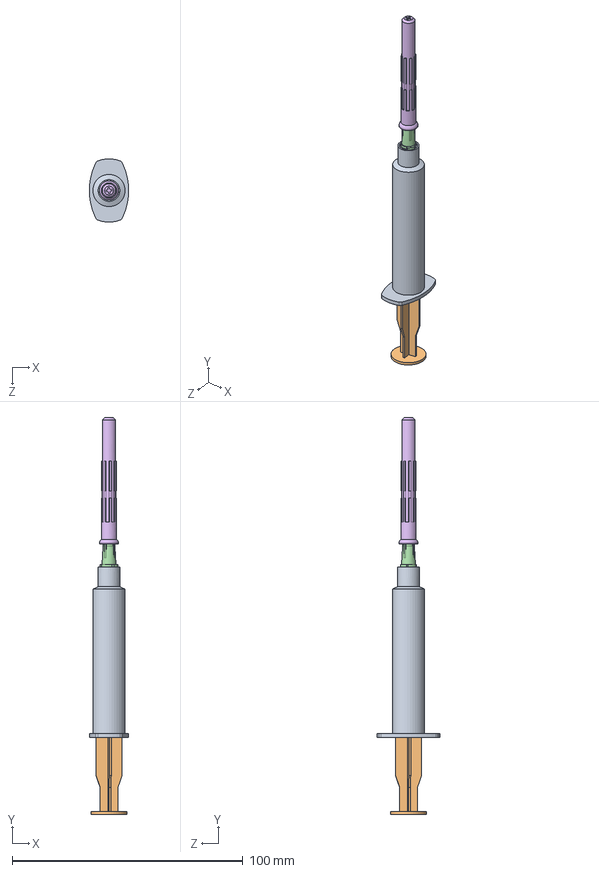
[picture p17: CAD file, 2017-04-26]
Hardware/Design/Medical/hypodermic-syringe-1.snapshot.3/Assem.SLDASM
17.0 x 172.1 x 27.4 mm
plunger
plunger_head
pin_mount
pin
closure

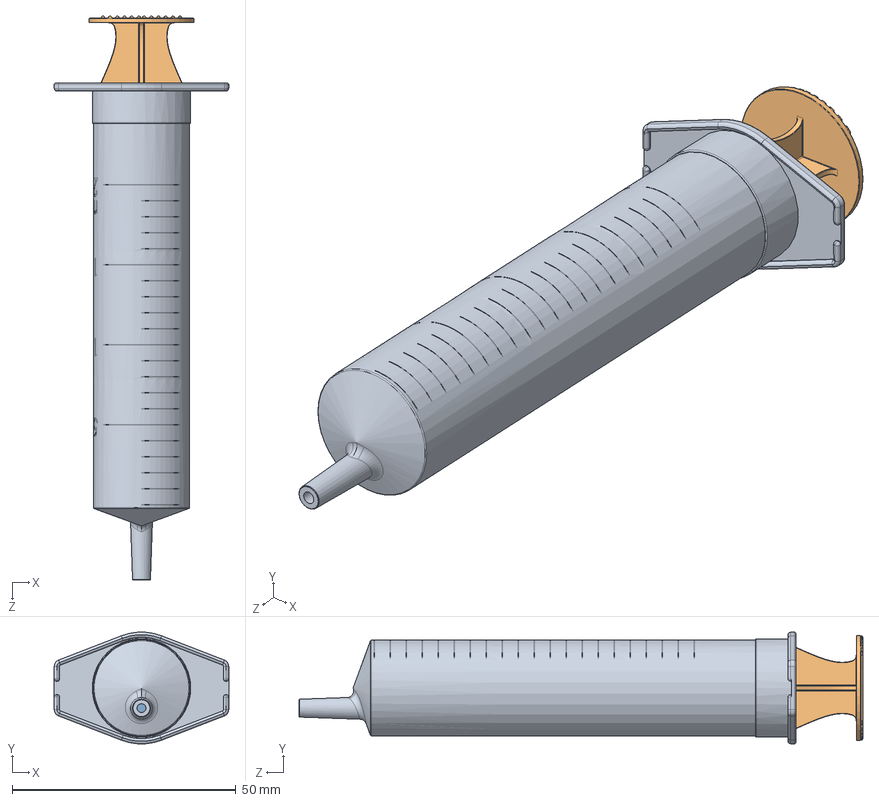
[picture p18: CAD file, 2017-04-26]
Hardware/Design/Medical/Pneumatic Syringe/syringe 20ml plastipak.SLDASM
39.0 x 24.9 x 126.0 mm
body 20ml
plunger
rubber plunger

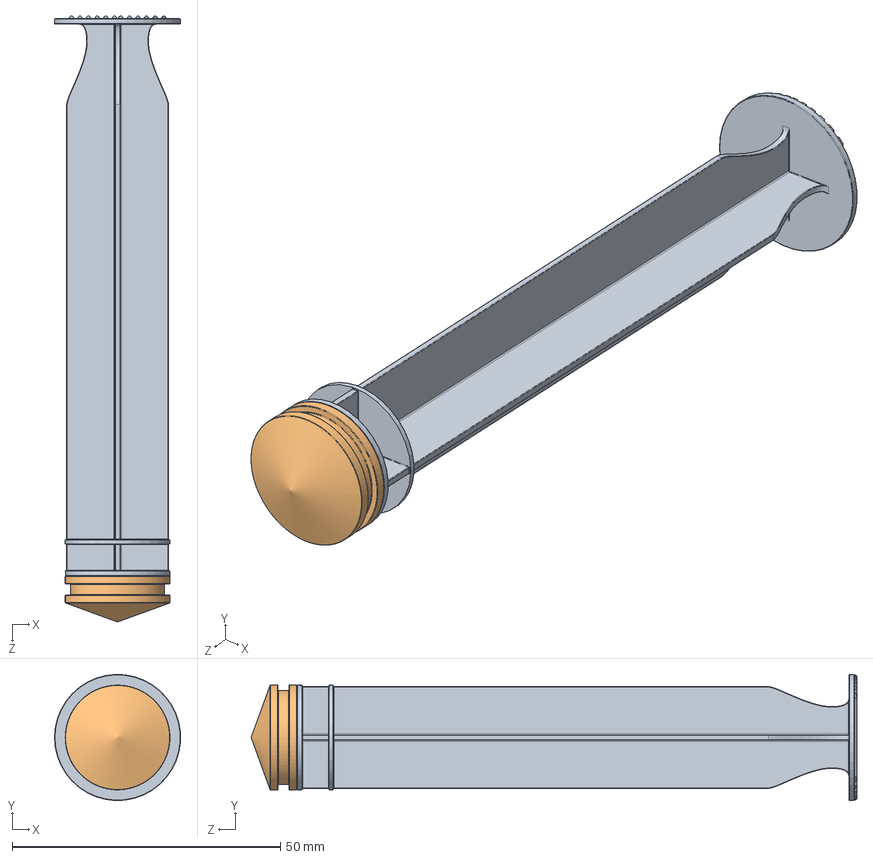
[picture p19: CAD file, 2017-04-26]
Hardware/Design/Medical/Syringe plastipak-20ml-syringe/syringe 20ml plastipak/Plunger Assembly.SLDASM
23.5 x 23.5 x 112.8 mm
plunger
rubber plunger

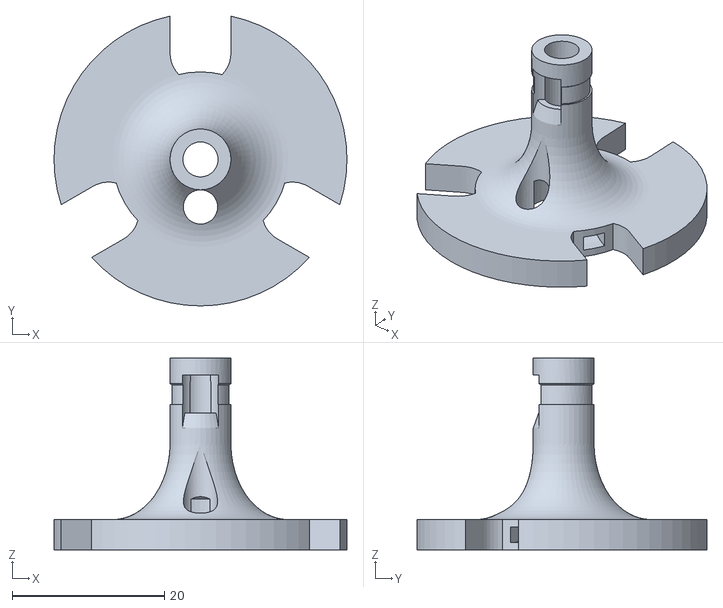
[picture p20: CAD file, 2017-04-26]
Hardware/Design/Needle_Mount/2-Component PLA Needle Mount/Needle Holder Assembly - NeedleMountBottom_Heated_Rev3_Standard-7.STL
38.5 x 38.1 x 25.2

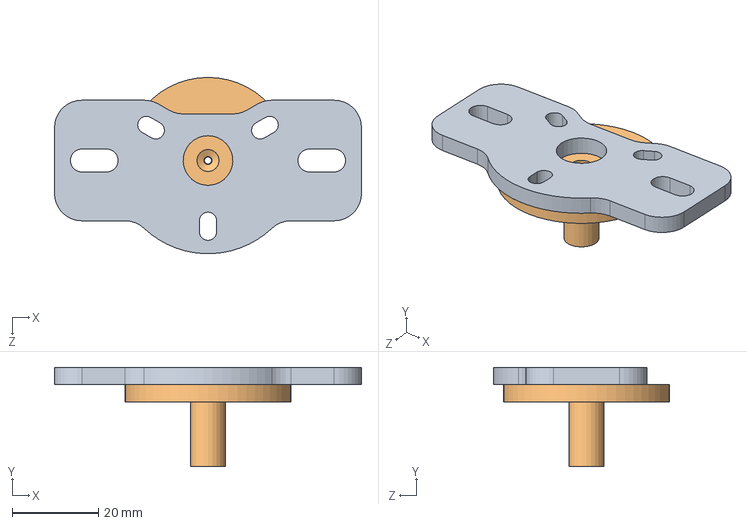
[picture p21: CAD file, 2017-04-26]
Hardware/Design/Needle_Mount/NeedleMountAssembly.sldasm
71.1 x 23.0 x 40.8 mm
NeedleMountTop
NeedleMountBottom

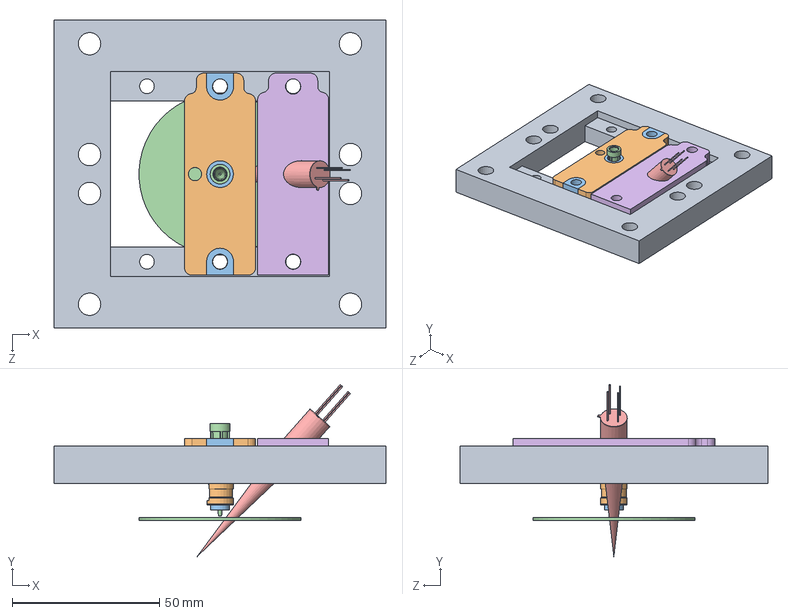
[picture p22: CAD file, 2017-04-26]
Hardware/Design/Needle_Mount/Square_Carrige/Mount and Gantries.SLDASM
112.6 x 58.4 x 104.6 mm
New Mount
New Mount Needle holder standard r1
New Mount Needle holder conductive r1
Qosina 11077
MLX90614ACF
IR sensor mount

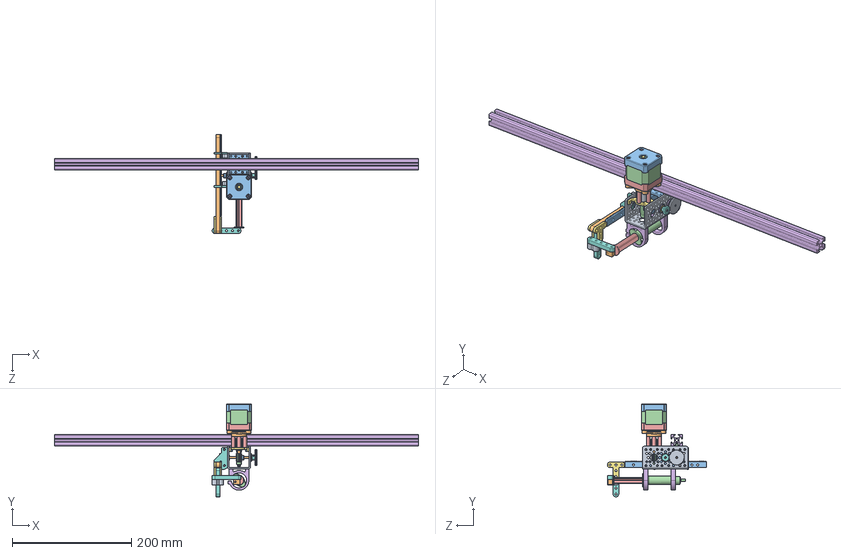
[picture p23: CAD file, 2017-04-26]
Hardware/Design/Syringe_Drive/Bioprinter_Syringe/Syringe_Gearbox.SLDASM
609.6 x 155.4 x 166.5 mm
Channel_3in_585442_a
NEMA17_motor_mount_555152_a
Base
Cuerpo
Tapa
pan cross head_am x 4
Eje
instrument ball bearing_68_am x 2
5mm_3-16in_coupling_625176
3-16_1in_shafting_634136_a
s1c83z-p048b055s_a
s1d94z-p048ss_a
6-32_Aluminum_Standoff x 4
Bearing_Adapter_633138_a x 5
0125_Bearing_535206_a x 4
s1063z-048s024_a
s1063z-048s048
a_7x_1_04023_a x 2
s5000y-12510_a
a_7x_8-c04016_a x 3
a_7x_8-c04031_a
a_1t_2-y32016
Hub_Mount_545424_a
Beam_Bracket_585656_a x 2
Beam_Blocks_585600_a x 4
6in_Beam_585416_a
Beam_Gear_Rack_615410_a_short
5mL_Syringe_Body
5mL_Syringe_pLUNGER
Tube_Clamp_1in_585434_a x 2
Beam_Bracket_F_585612_a x 2
1p5_Beam_585404_a x 2
Beam_90_Bracket_585490_a
Attachment_Blocks_585400_a
Quad_Mount_C_545360_a
M5_10mm_SocketHead_90128A234
5M_FenderWasher_15mm_91116A140
80-20_Tslot_Framing_2ft_5537T104

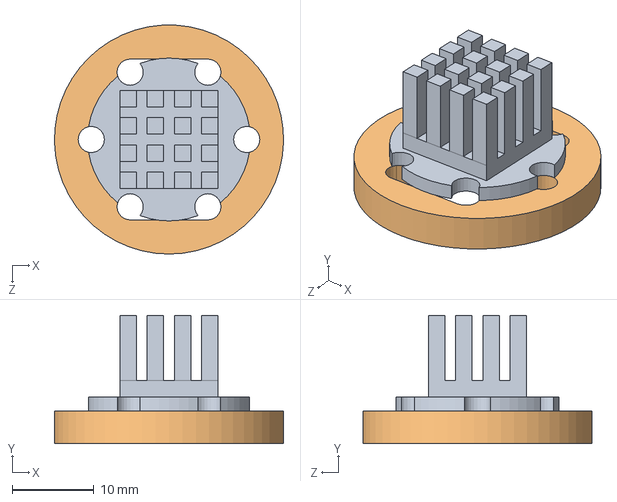
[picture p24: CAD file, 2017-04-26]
Hardware/Design/UV/UV_Star_rev1.SLDASM
28.0 x 15.7 x 28.0 mm
UV_Star
UV_Star_Holder

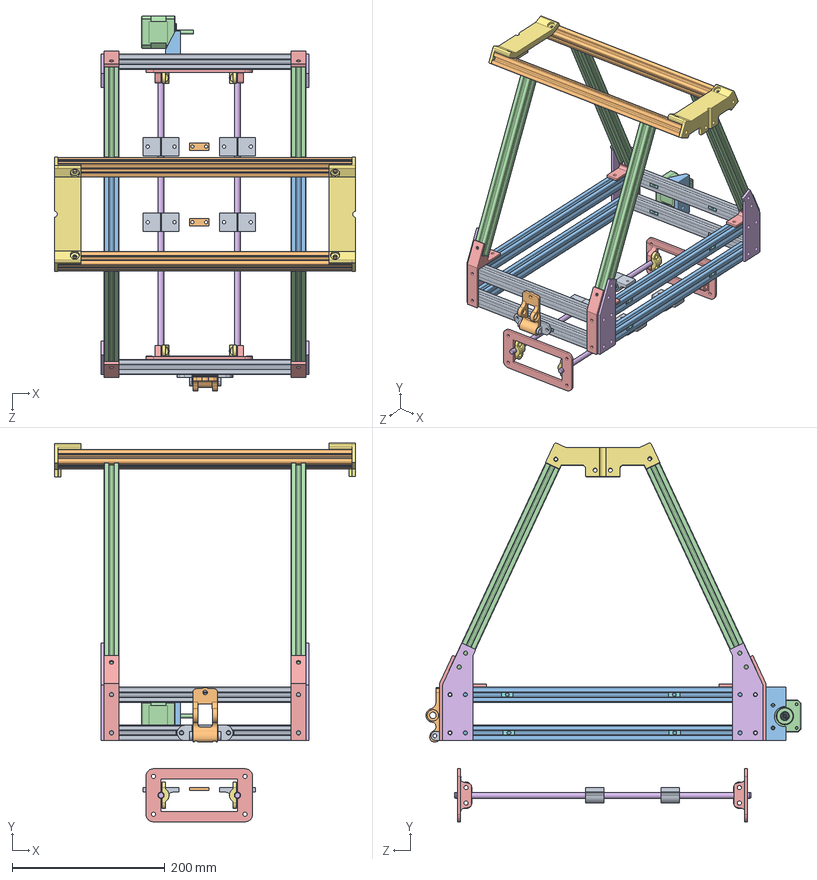
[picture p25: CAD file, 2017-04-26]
Solidworks_Files/Solidworks_Files_Green_Team/MS_1/Assembly/MS1 Assembly.SLDASM
395.0 x 496.3 x 491.3 mm
2020 T-Slotted Frame (x-axis-265mm) x 4
2020 T-Slotted Frame (x-axis-385mm) x 2
2020 T-Slotted Frame (y-axis-380mm) x 4
2020 T-Slotted Frame (yz-axis-300mm) x 4
Lower Middle Vertex x 4
Lower Left-Right Vertex x 4
Z Upper Idler x 2
T Nut x 21
Y Tensioner Mount
Y Idler Tensioner
Y Motor Mount
Motor
Y Rod Mount x 2
Steel Rod x 2
Z Rod Clamp x 4
LM8UU Bearing x 4
LM8UU Bearing Holder x 4
Y Belt Clamp x 2

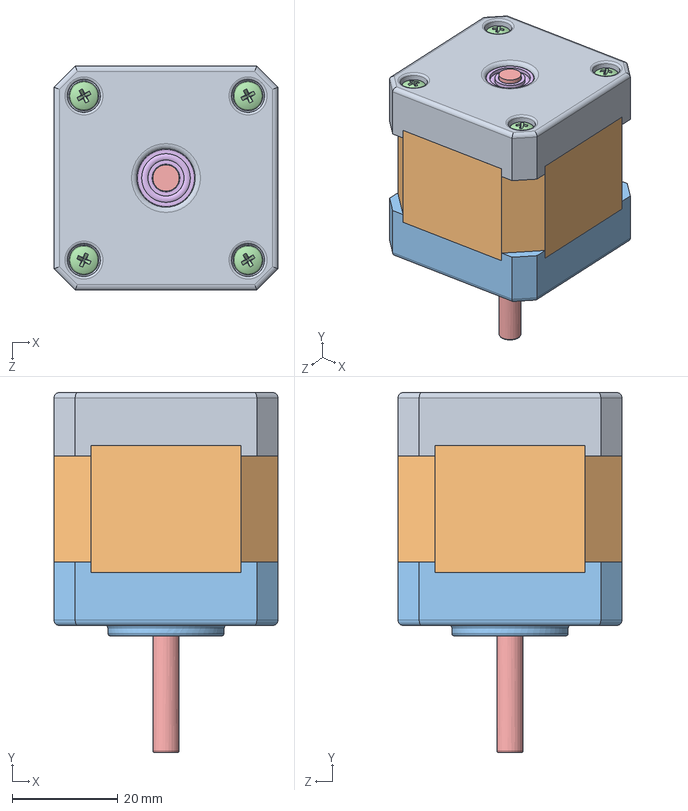
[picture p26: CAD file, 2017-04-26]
Solidworks_Files/Solidworks_Files_Green_Team/MS_4/Assembly/MS4 - SubAssembly - Motor Mount.SLDASM
42.3 x 68.0 x 42.3 mm
Base
Cuerpo
Tapa
pan cross head_am x 4
Eje
instrument ball bearing_68_am x 2

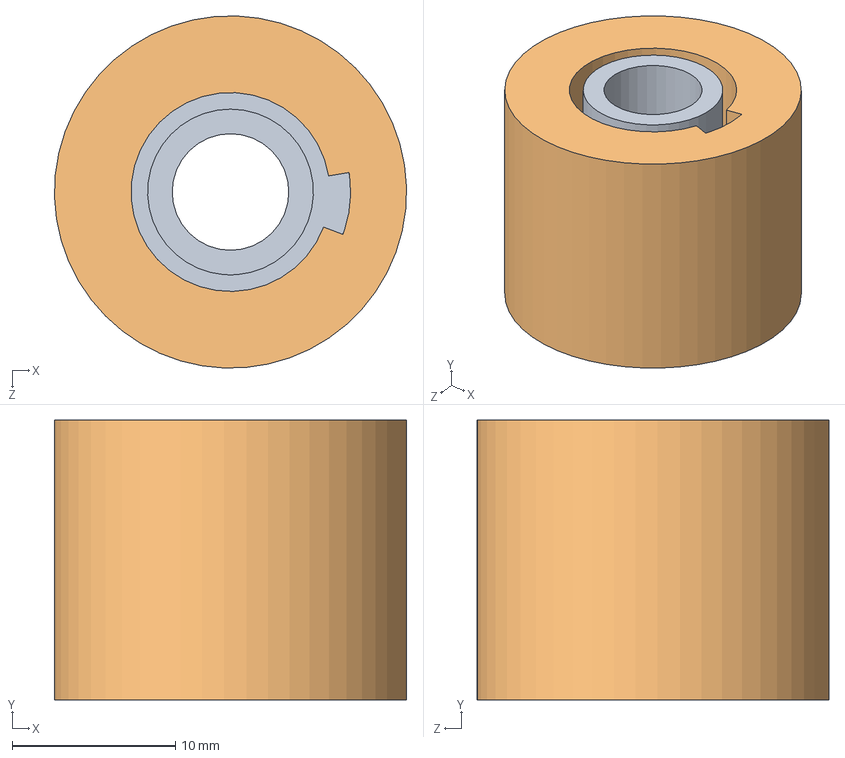
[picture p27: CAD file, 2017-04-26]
Solidworks_Files/Solidworks_Files_Green_Team/MS_5/Assembly/CarbonFiber_Sleeve_NoTemp.SLDASM
21.6 x 17.1 x 21.6 mm
Inner
Outer-No temp

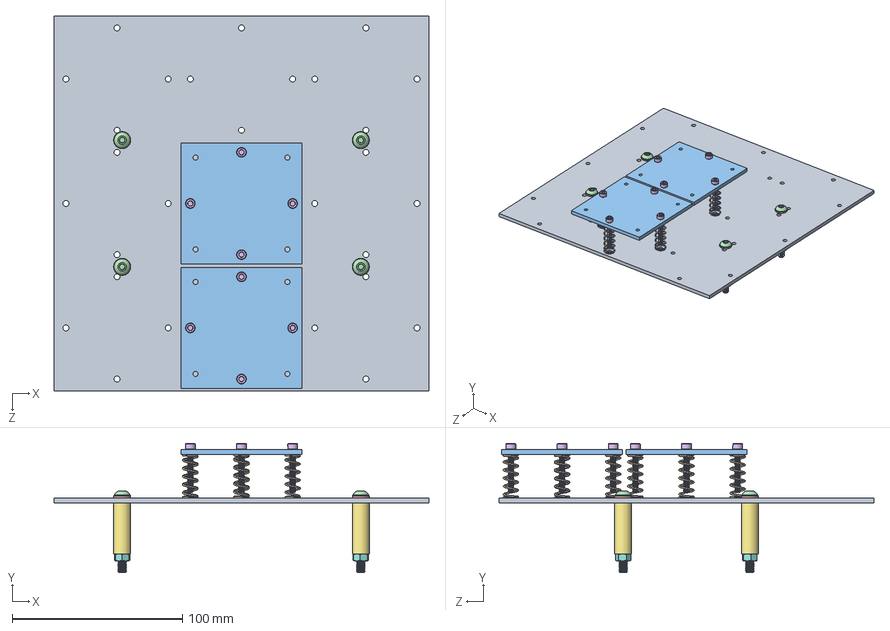
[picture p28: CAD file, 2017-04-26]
Solidworks_Files/Solidworks_Files_Green_Team/MS_6/Assembly/Stage Plate Assembly.SLDASM
220.0 x 75.8 x 220.0 mm
Large Stage Plate
Spring x 8
Small Stage Plate x 2
M5 Bolt x 4
M5 Washer x 4
6-32 Bolt x 8
Spacer x 4
M5 Nut x 4

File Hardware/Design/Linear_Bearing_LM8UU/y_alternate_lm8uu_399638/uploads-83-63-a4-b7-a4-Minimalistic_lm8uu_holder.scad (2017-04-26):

//******************
//Adjustable Variables
//******************

$fn =30;
lmuuOuterD = 15;
ShellSize = 3;
MBoltSize = 3;
MountHolesCenters = 25;
BaseOffset = 0.2;
MountThickness = 5;
HolderWidthMultiplier = 2; 

//******************

//Other Variables Used
MountLength = MountHolesCenters+(MBoltSize*2)+(ShellSize*2);
HolderWidth = MBoltSize+(HolderWidthMultiplier*ShellSize);

difference()
{
	union()
	{
//Outer Cylinder
		translate([0,0,HolderWidth/2])
			cylinder(r=lmuuOuterD/2 +ShellSize,h =HolderWidth,center=true);
//Base Mounting
		translate([MountLength/-2,(lmuuOuterD/2)-BaseOffset-MountThickness,0])
			cube([MountLength,MountThickness,HolderWidth]);
		
	}
//Bottom Cut
	translate([(lmuuOuterD+ShellSize)/-2,(lmuuOuterD/2)-BaseOffset,0])
			cube([lmuuOuterD+(ShellSize),ShellSize*2,HolderWidth]);
	
//Inner Cylinder
	translate([0,0,HolderWidth/2])
		cylinder(r = lmuuOuterD/2,h = HolderWidth+0.1, center = true);
	
//Mounting Hole1
	translate([MountHolesCenters/2,(lmuuOuterD/2)-BaseOffset-(MountThickness/2),HolderWidth/2])
	{
		cube([MBoltSize*2,MountThickness+0.2,MBoltSize],center=true);
	rotate([90,0,0])
		translate([0,0,MountThickness/2])
		cylinder(r=MBoltSize+0.5,h=10);
	}
//Mirror of Mounting Hole1
	mirror([1,0,0]){
		translate([MountHolesCenters/2,(lmuuOuterD/2)-BaseOffset-(MountThickness/2),HolderWidth/2])
		{
			cube([MBoltSize*2,MountThickness+0.2,MBoltSize],center=true);
		rotate([90,0,0])
			translate([0,0,MountThickness/2])
				cylinder(r=MBoltSize+0.5,h=10);
		}
	}

//Blunt the pointy bits
	translate([0,(lmuuOuterD/2)-BaseOffset-ShellSize/2,HolderWidth/2])
			cube([ShellSize*4,ShellSize,HolderWidth], center = true);
}

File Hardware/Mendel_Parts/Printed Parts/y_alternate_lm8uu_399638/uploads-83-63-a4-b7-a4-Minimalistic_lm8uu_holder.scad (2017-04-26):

//******************
//Adjustable Variables
//******************

$fn =30;
lmuuOuterD = 15;
ShellSize = 3;
MBoltSize = 3;
MountHolesCenters = 25;
BaseOffset = 0.2;
MountThickness = 5;
HolderWidthMultiplier = 2; 

//******************

//Other Variables Used
MountLength = MountHolesCenters+(MBoltSize*2)+(ShellSize*2);
HolderWidth = MBoltSize+(HolderWidthMultiplier*ShellSize);

difference()
{
	union()
	{
//Outer Cylinder
		translate([0,0,HolderWidth/2])
			cylinder(r=lmuuOuterD/2 +ShellSize,h =HolderWidth,center=true);
//Base Mounting
		translate([MountLength/-2,(lmuuOuterD/2)-BaseOffset-MountThickness,0])
			cube([MountLength,MountThickness,HolderWidth]);
		
	}
//Bottom Cut
	translate([(lmuuOuterD+ShellSize)/-2,(lmuuOuterD/2)-BaseOffset,0])
			cube([lmuuOuterD+(ShellSize),ShellSize*2,HolderWidth]);
	
//Inner Cylinder
	translate([0,0,HolderWidth/2])
		cylinder(r = lmuuOuterD/2,h = HolderWidth+0.1, center = true);
	
//Mounting Hole1
	translate([MountHolesCenters/2,(lmuuOuterD/2)-BaseOffset-(MountThickness/2),HolderWidth/2])
	{
		cube([MBoltSize*2,MountThickness+0.2,MBoltSize],center=true);
	rotate([90,0,0])
		translate([0,0,MountThickness/2])
		cylinder(r=MBoltSize+0.5,h=10);
	}
//Mirror of Mounting Hole1
	mirror([1,0,0]){
		translate([MountHolesCenters/2,(lmuuOuterD/2)-BaseOffset-(MountThickness/2),HolderWidth/2])
		{
			cube([MBoltSize*2,MountThickness+0.2,MBoltSize],center=true);
		rotate([90,0,0])
			translate([0,0,MountThickness/2])
				cylinder(r=MBoltSize+0.5,h=10);
		}
	}

//Blunt the pointy bits
	translate([0,(lmuuOuterD/2)-BaseOffset-ShellSize/2,HolderWidth/2])
			cube([ShellSize*4,ShellSize,HolderWidth], center = true);
}

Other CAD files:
Hardware/Design/Needle_Mount/Square_Carrige/New Mount Needle holder Assembly Conductive.STL
Hardware/Design/3mL_Syringe_Plunger_Attachment/Attachment_Blocks_585400_a.SLDPRT
Hardware/Design/3mL_Syringe_Plunger_Attachment/Plunger_Flange.SLDPRT
Hardware/Design/3mL_Syringe_Plunger_Attachment/STL_Files/Part1^3mL_Syringe_Plunger_Attachment.STL
Hardware/Design/3mL_Syringe_Plunger_Attachment/STL_Files/Part2^3mL_Syringe_Plunger_Attachment.STL
Hardware/Design/CarbonFiber_Sleeve_Brackets/Inner.SLDPRT
Hardware/Design/CarbonFiber_Sleeve_Brackets/Inner.STL
Hardware/Design/CarbonFiber_Sleeve_Brackets/Insulator.SLDPRT
Hardware/Design/CarbonFiber_Sleeve_Brackets/Insulator.STL
Hardware/Design/CarbonFiber_Sleeve_Brackets/Outer-No temp.SLDPRT
Hardware/Design/CarbonFiber_Sleeve_Brackets/Outer-No temp.STL
Hardware/Design/CarbonFiber_Sleeve_Brackets/Outer2-Temp.SLDPRT
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

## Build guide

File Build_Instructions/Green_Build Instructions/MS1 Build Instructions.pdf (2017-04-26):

# A - Short End of Base (with Motor): Parts

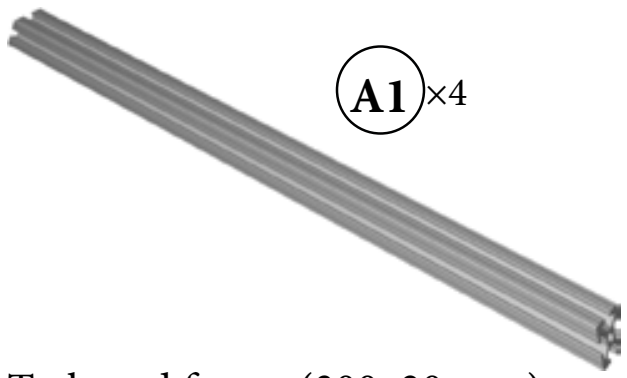
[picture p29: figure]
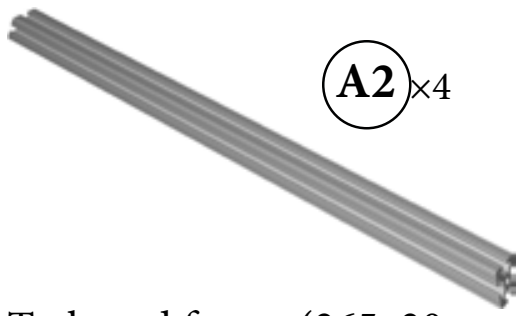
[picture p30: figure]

## M5x14 Bolt

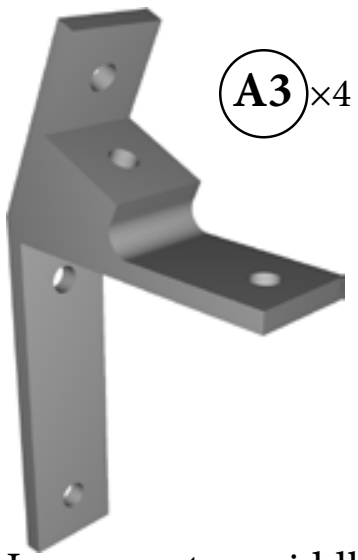
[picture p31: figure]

## M5x10 Bolt

## M5 Washer

## Lower vertex middle

## T-slotted frame (265x20 mm)

## T-slotted frame (300x20 mm)

## T-nut

A5 ×16

A4 ×12
A7 ×4
A6 ×25

# Milestone 1 Building Instructions Ryan Brody

Anthony Caffaro
Robin Cross
Aimee Lam
Ava Mistry
Patrick Stevenson
Rachelle Walter

# B - Long End of Base: Parts

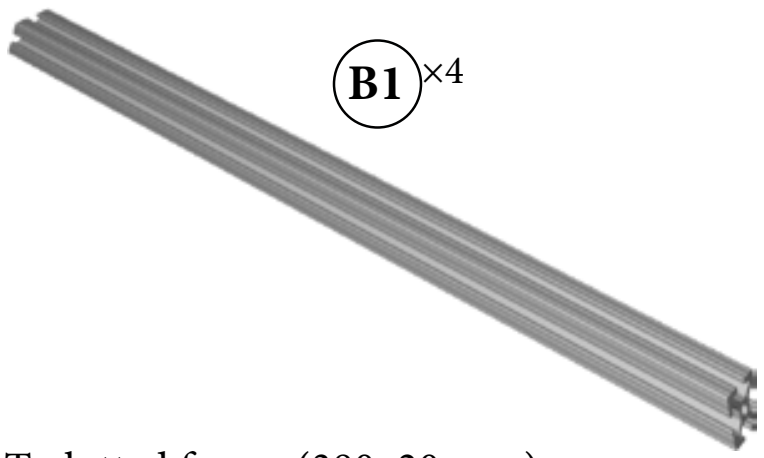
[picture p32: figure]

## T-slotted frame (380x20 mm)

B2 ×4

## M5x10 Bolt

## M5 Washer

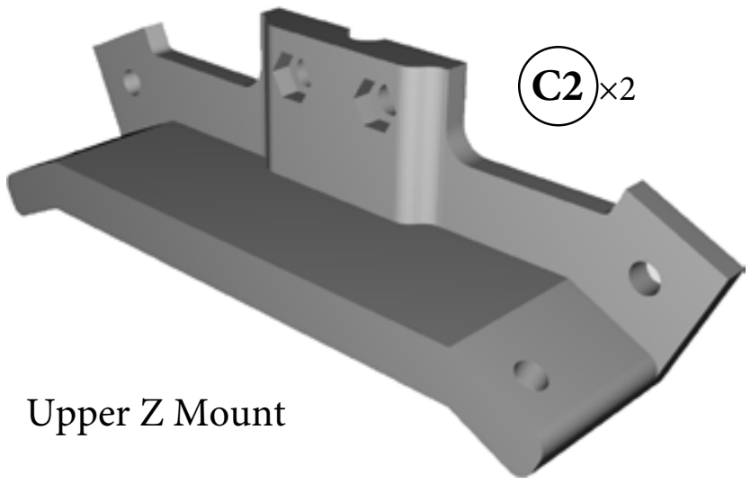
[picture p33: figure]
Upper Z Mount

A5 ×28

A4 ×28

## Lower vertex left/right

## T-nut

A6 ×28

# C - Top of Frame: Parts

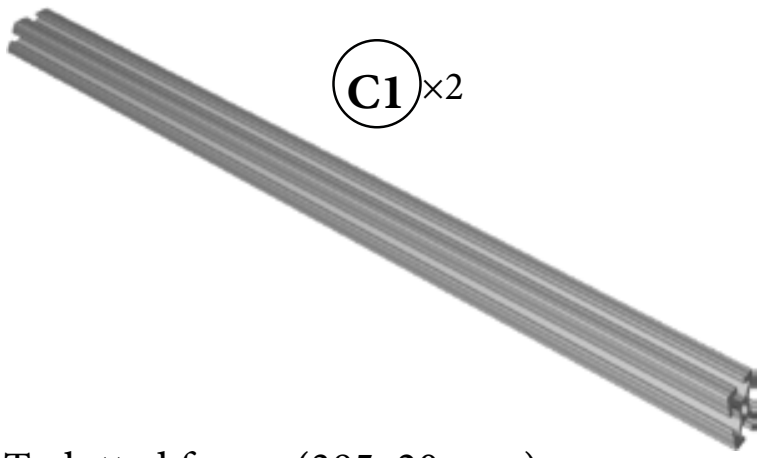
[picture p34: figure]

## T-slotted frame (385x20 mm)

M5x10 Bolt | M5 Washer
A4 | A5 ×8

×8

C3 ×4

## Button head M5x16 Bolt

## T-nut

A6 ×5

# D - Y-Axis Base: Parts

## Rod clamp

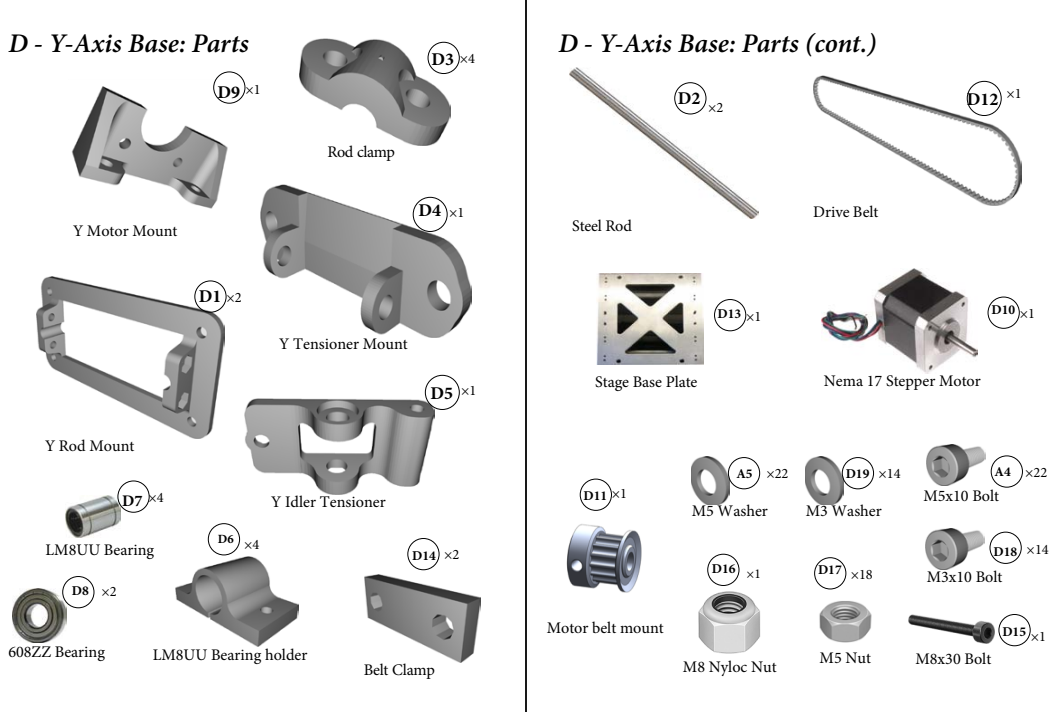
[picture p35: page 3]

D - Y-Axis Base: Parts (cont.)

# A - Short End of Base: Assembly A - Short End of Base: Assembly

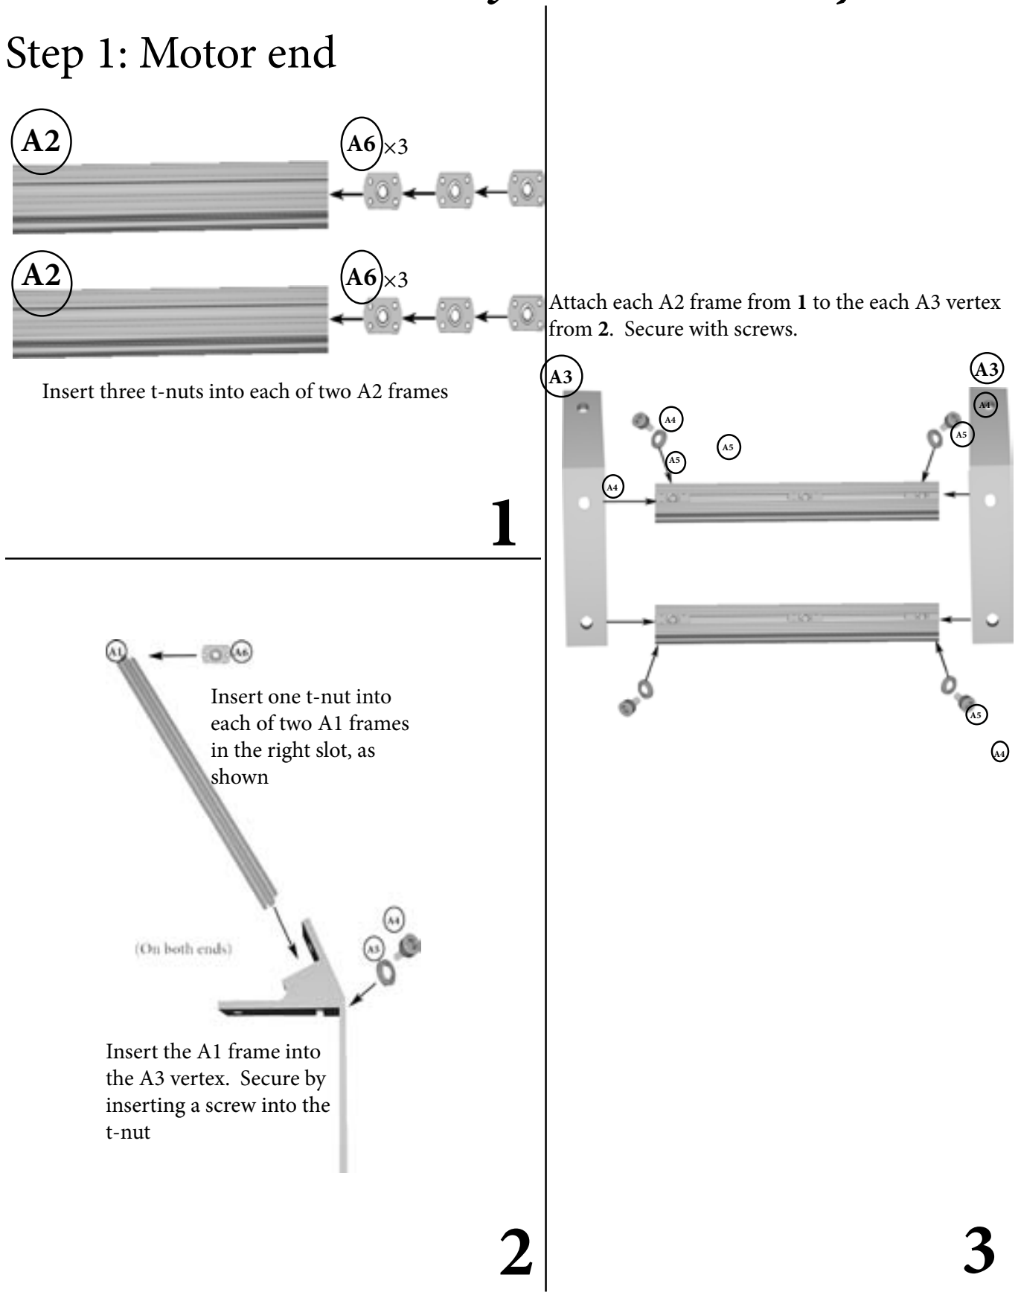
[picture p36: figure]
Step 1: Motor end; Insert one t-nut into each of two A1 frames in the right slot, as shown; Insert the A1 frame into the A3 vertex. Secure by inserting a screw into the t-nut; from 2. Secure with screws.

Insert three t-nuts into each of two A2 frames

Attach each A2 frame from 1 to the each A3 vertex

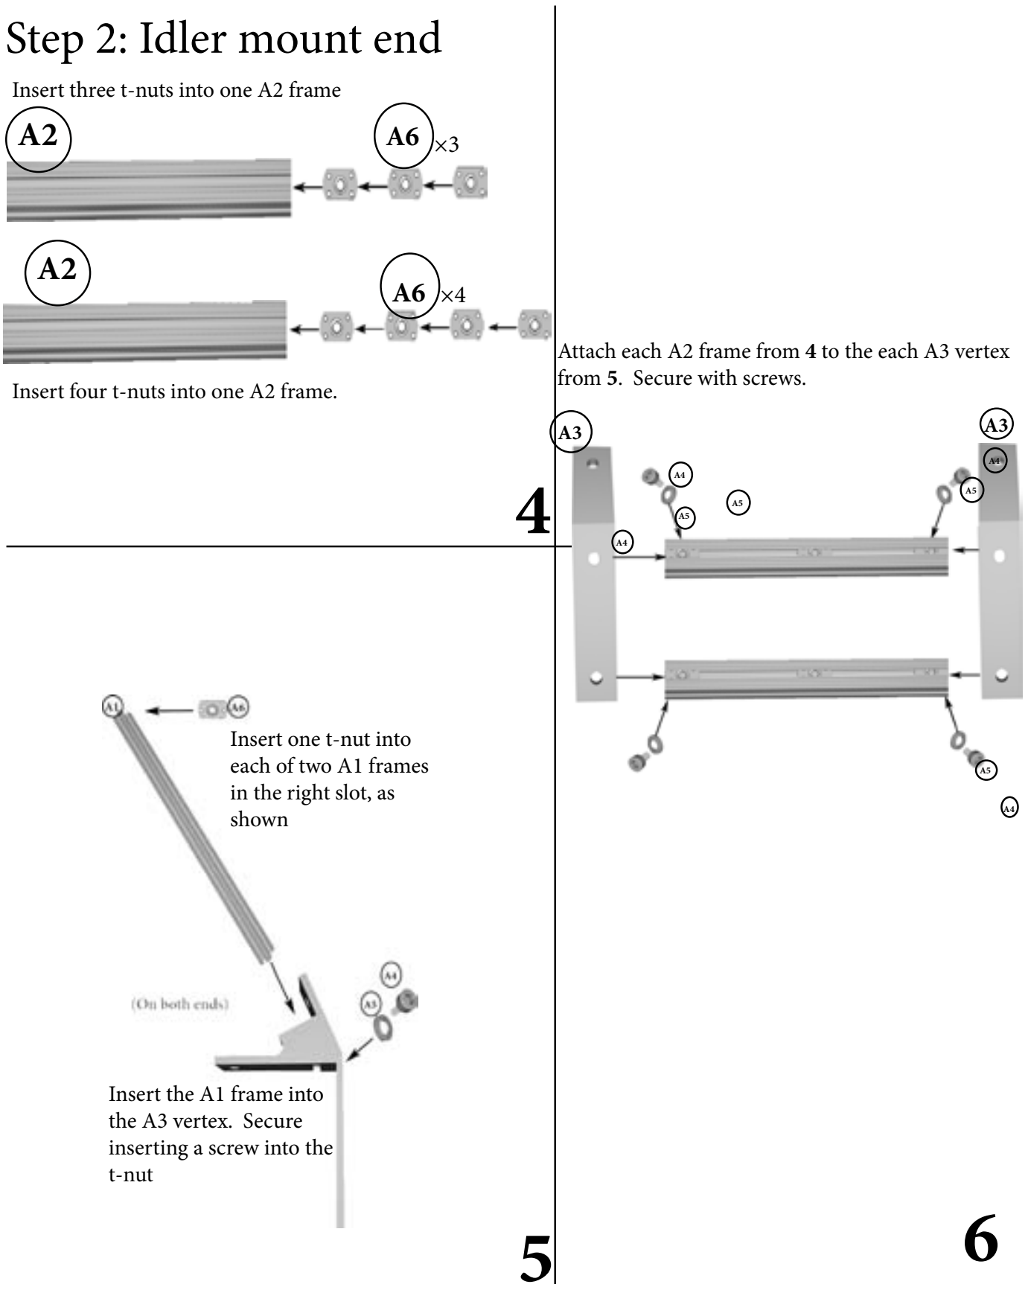
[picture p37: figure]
Step 2: Idler mount end; Insert four t-nuts into one A2 frame.; Insert three t-nuts into one A2 frame; Insert one t-nut into each of two A1 frames in the right slot, as shown; Insert the A1 frame into the A3 vertex. Secure inserting a screw into the t-nut; from 5. Secure with screws.

Attach each A2 frame from 4 to the each A3 vertex

# B - Long End of Base: Assembly

B1 ×3 | A6 ×4

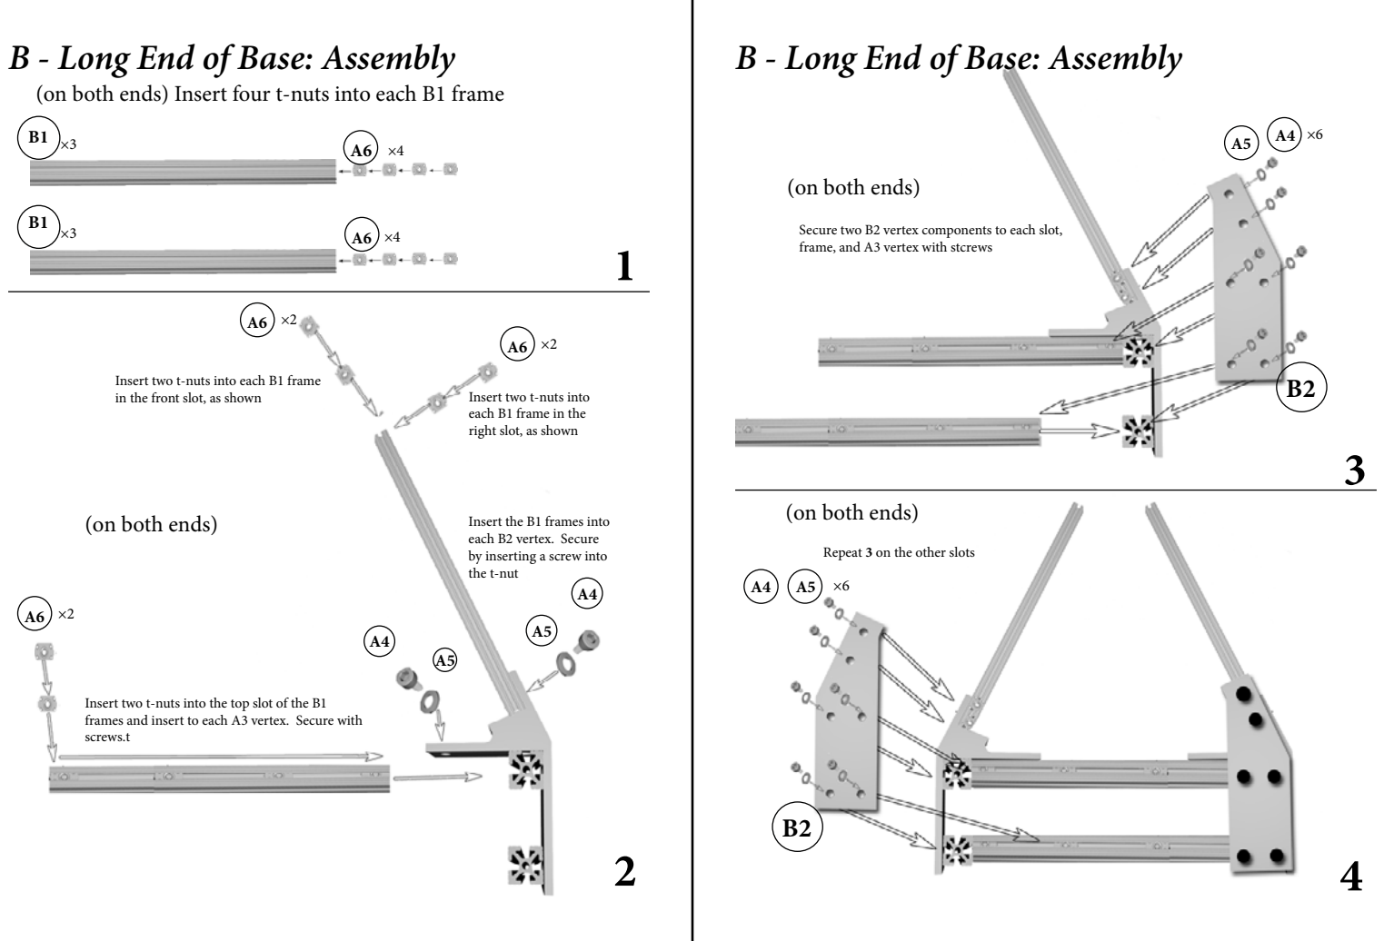
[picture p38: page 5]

## (on both ends) Insert four t-nuts into each B1 frame

B1 ×3 | A6 ×4

A6 ×2

A6 ×2

A6 ×2

A4
A5 A4
A5

1

2

## (on both ends)

## (on both ends)

A5

×6

B2

Repeat 3 on the other slots
A4 A5 ×6

B2

3

4

## (on both ends)

# B - Long End of Base: Assembly

Insert two t-nuts into
each B1 frame in the
right slot, as shown

Insert two t-nuts into each B1 frame in the front slot, as shown

Insert the B1 frames into
each B2 vertex. Secure
by inserting a screw into
the t-nut

Insert two t-nuts into the top slot of the B1 frames and insert to each A3 vertex. Secure with screws.t

Secure two B2 vertex components to each slot, frame, and A3 vertex with stcrews

A4

# C - Top of Frame: Assembly

A6 ×2

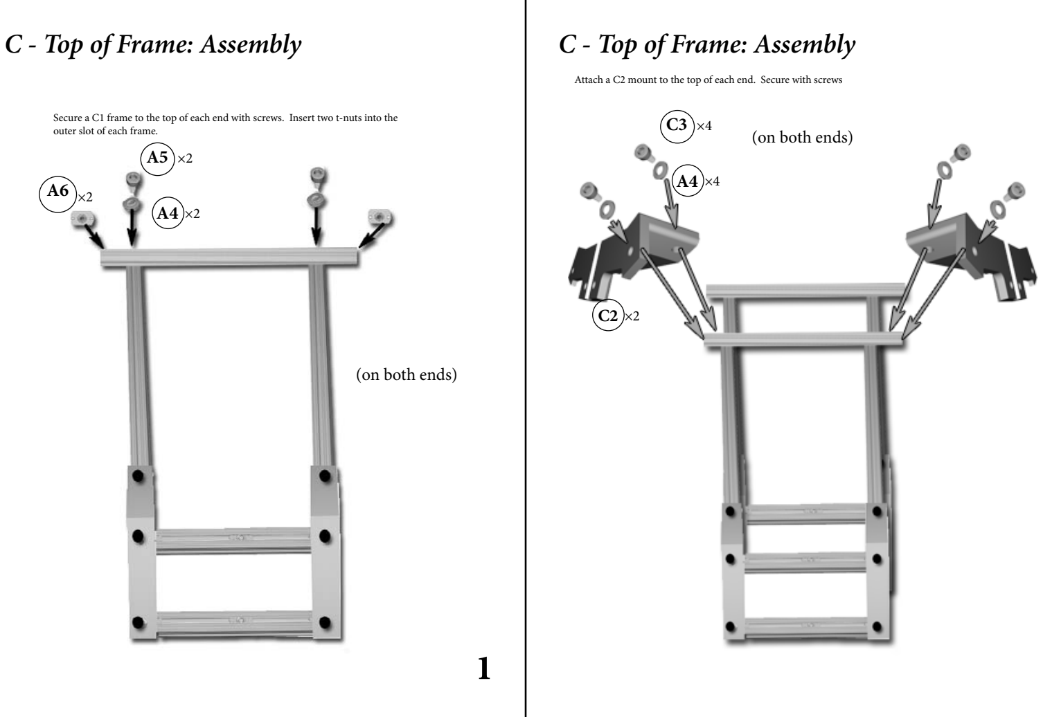
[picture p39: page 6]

A4 ×2

A5 ×2

1

## (on both ends)

## (on both ends)

A4 ×4

C3 ×4

C2 ×2

# C - Top of Frame: Assembly

Secure a C1 frame to the top of each end with screws. Insert two t-nuts into the outer slot of each frame.

Attach a C2 mount to the top of each end. Secure with screws

# D - Y-axis base: Assembly

# Step 1: Motor end

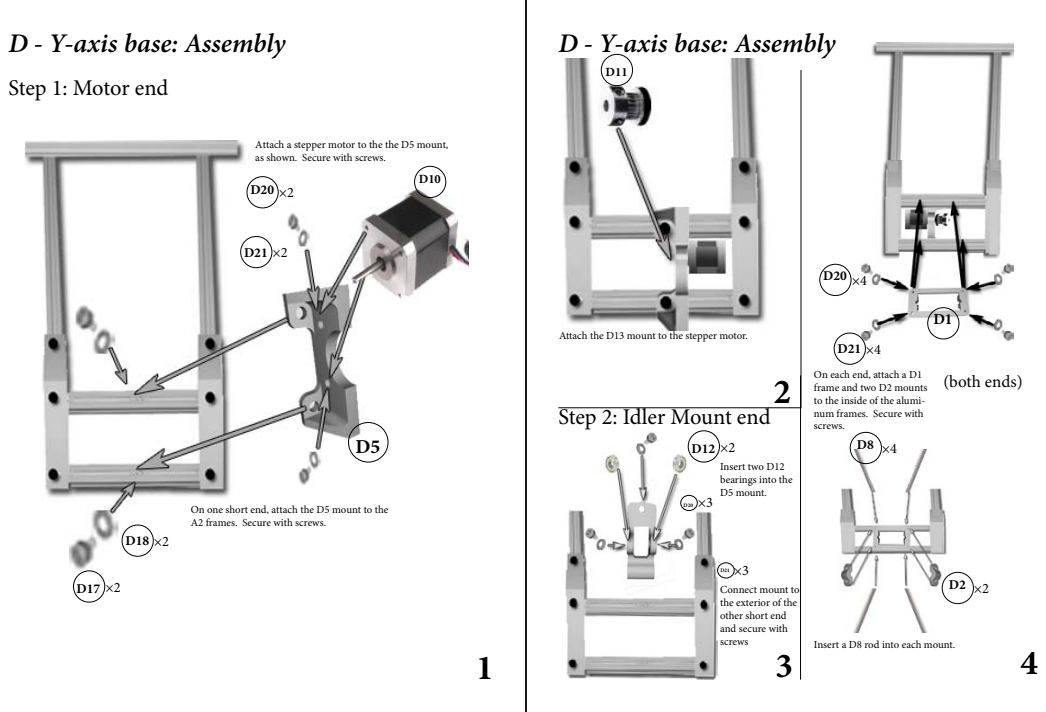
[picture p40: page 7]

Attach a stepper motor to the the D5 mount,
as shown. Secure with screws.

Attach the D13 mount to the stepper motor.

frame and two D2 mounts
to the inside of the alumi-
num frames. Secure with
screws.

On each end, attach a D1

Step 2: Idler Mount end

On one short end, attach the D5 mount to the
A2 frames. Secure with screws.

Connect mount to
the exterior of the
other short end
and secure with
screws

Insert a D8 rod into each mount.

# D - Y-axis base: Assembly

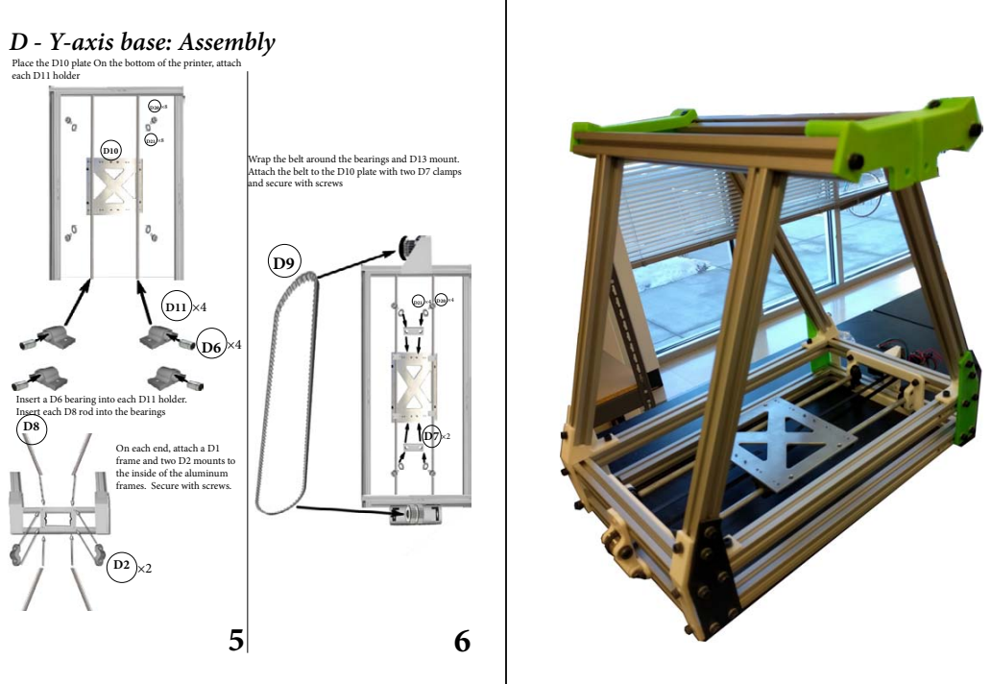
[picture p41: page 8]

Place the D10 plate On the bottom of the printer, attach
each D11 holder

Wrap the belt around the bearings and D13 mount.
Attach the belt to the D10 plate with two D7 clamps
and secure with screws

Insert a D6 bearing into each D11 holder.
Insert each D8 rod into the bearings

On each end, attach a D1
frame and two D2 mounts to
the inside of the aluminum
frames. Secure with screws.

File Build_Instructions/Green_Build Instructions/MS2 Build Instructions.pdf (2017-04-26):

# Milestone 2 Building Instructions

### Ryan Brody

### Robin Cross

### Anthony Caffaro

### Aimee Lam

### Ava Mistry

### Patrick Stevenson

### Rachelle Walter

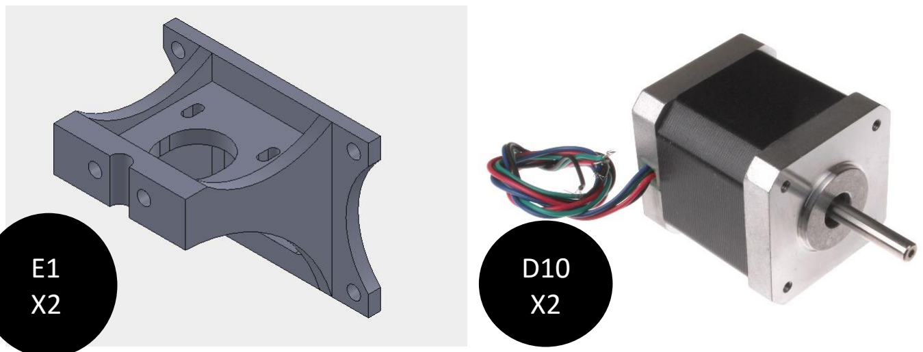
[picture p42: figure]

A7
X8

# Y Axis Motor Mount (both sides): Parts

Lower Z motor mount | Nema 17 Stepper Motor

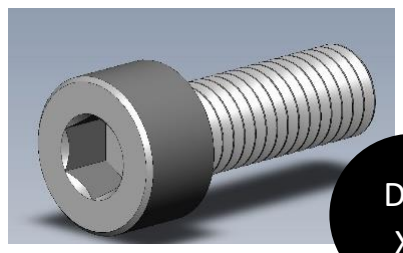
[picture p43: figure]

M5 X 14mm bolt | M3 X 10mm bolt
M5 washer | M3 Washer

D21
X8

D20
X8

A5
X8

# Y Rods and clamp for z axis (Non-motor side): Parts

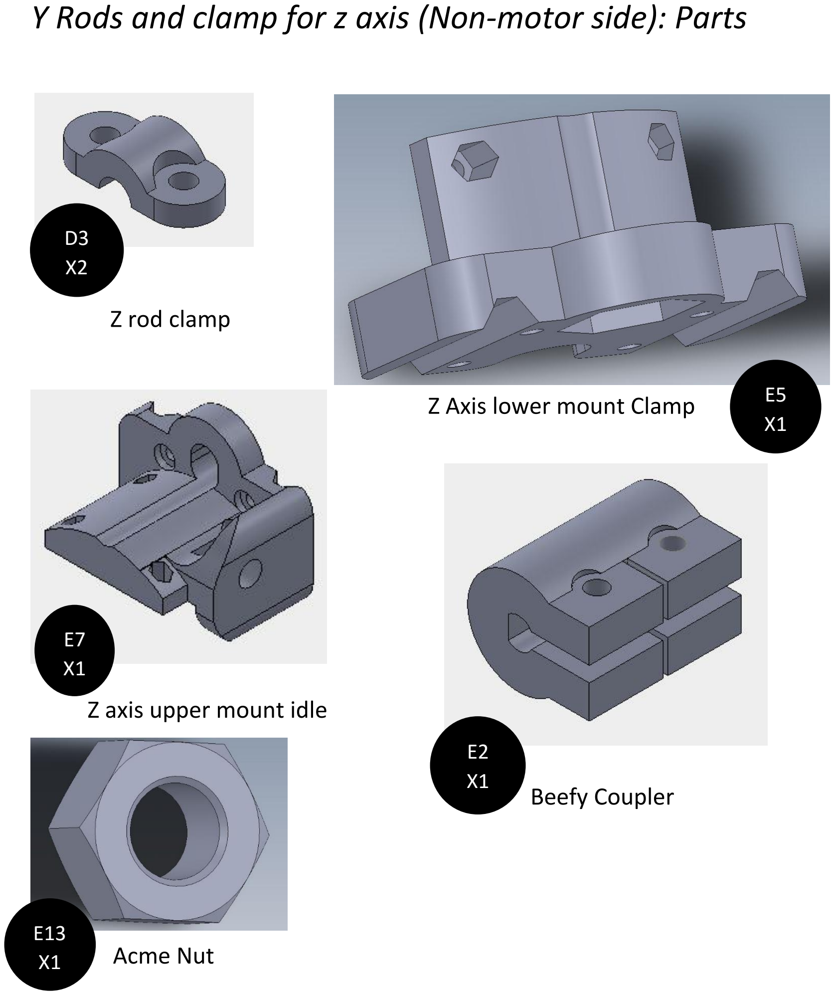
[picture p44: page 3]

## Acme Nut

## Z rod clamp

## Z Axis lower mount Clamp

## Z axis upper mount idle

## Beefy Coupler

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
# Y Rods and clamp for z axis (Non-motor side): Parts

Contd.

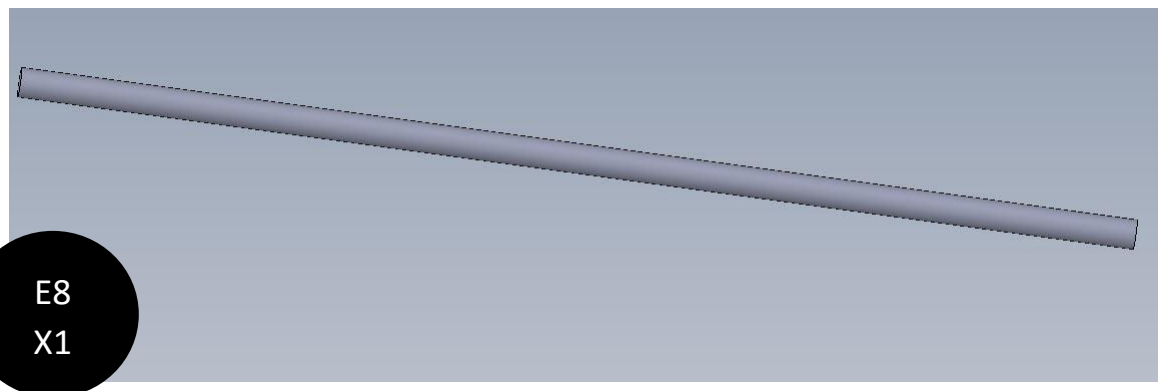
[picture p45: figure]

## Z steel Rod

## Threaded Rod

## M3 X 20mm

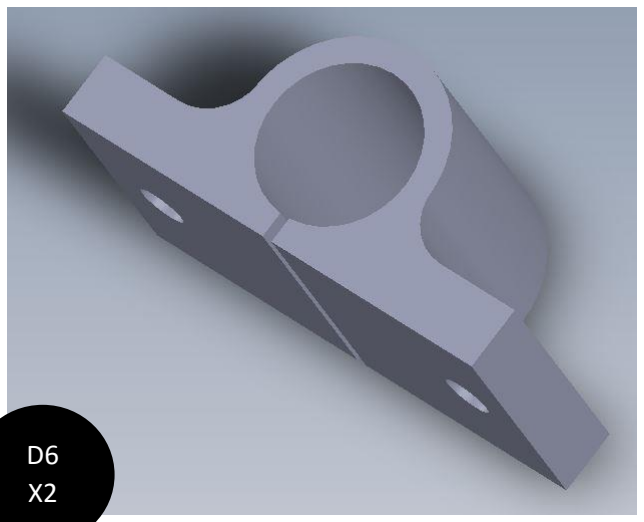
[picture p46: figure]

## LM8UU Bearing Holder

## M3 X 16 mm

## LM8UU Bearing

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
## M3 Lock Nut

## M3 Nut

## M3 Washer

D21
X10

A7
X4

# Y Rods and clamp for z axis (Non-motor side): Parts

Contd.

M8 X 30 mm Bolt | M5 X 14 mm Bolt
M8 Locknut | M5 Washer

## 6082Z Bearing

D15
X1

D16

D8

A5
X4

# Y Rods and clamp for Z axis (Motor side): Parts

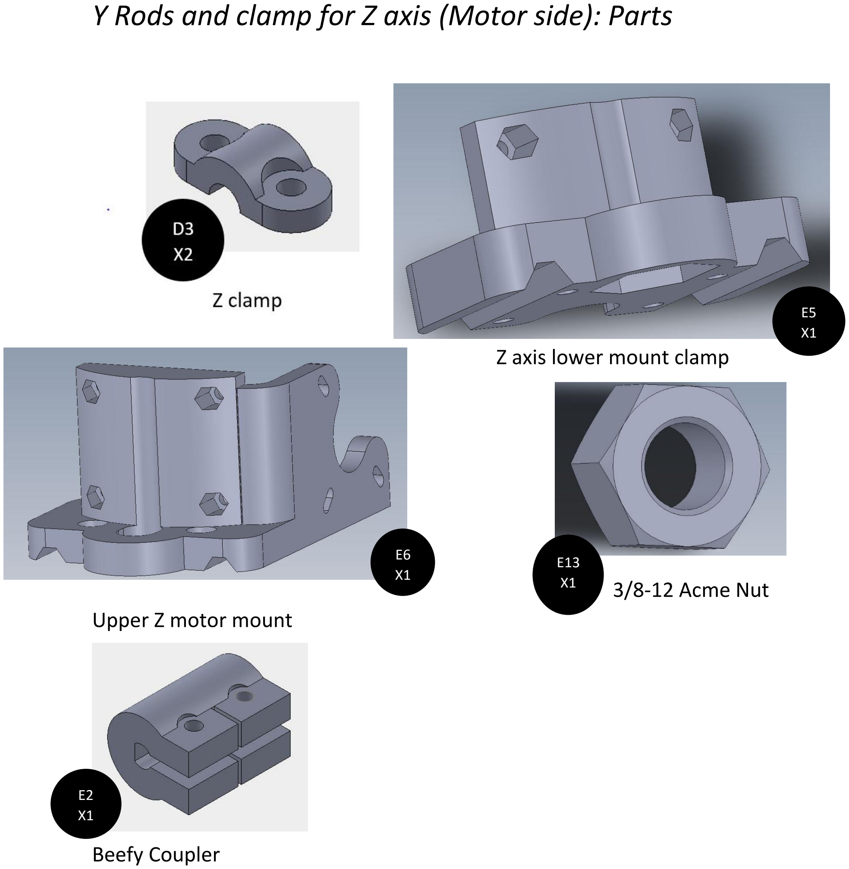
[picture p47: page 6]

## Z axis lower mount clamp

## Upper Z motor mount

## Beefy Coupler

E5
X1

E6
X1

## 3/8-12 Acme Nut

E13
X1

E2
X1

# Y Rods and clamp for z axis (motor side): Parts

Contd.

## Z steel Rod

## Threaded Rod

## M3 X 20mm

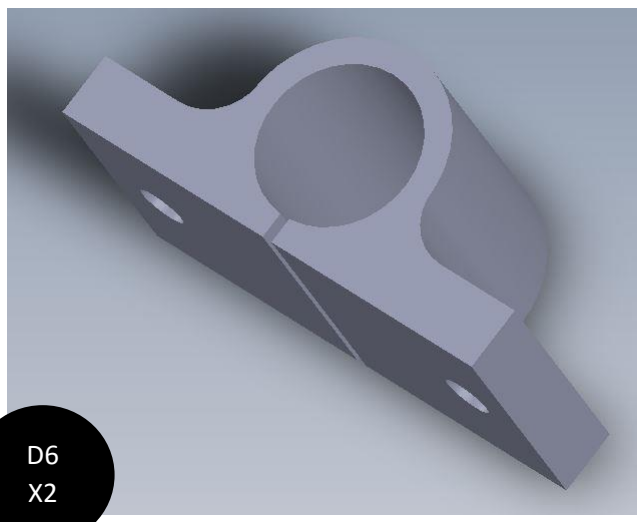
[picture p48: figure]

## LM8UU Bearing Holder

## M3 X 16 mm

## LM8UU Bearing

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
## M3 Lock Nut

## M3 Nut

## M3 Washer

D21
X8

A7
X4

# Y Rods and clamp for z axis (motor side): Parts

Contd.

M3 X 10mm | M3 Washer | M5 X 14mm Bolt

## M5 Washer

## T5 Pulley

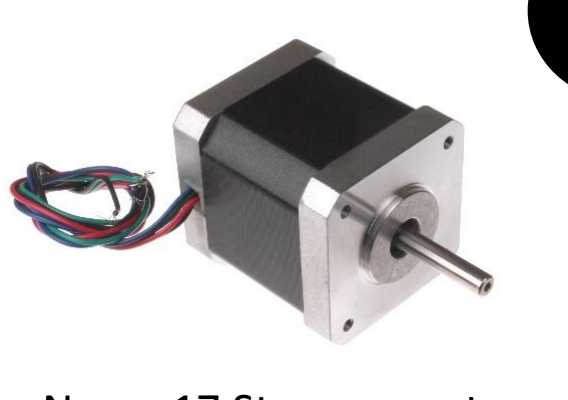
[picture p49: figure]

## Nema 17 Stepper motor

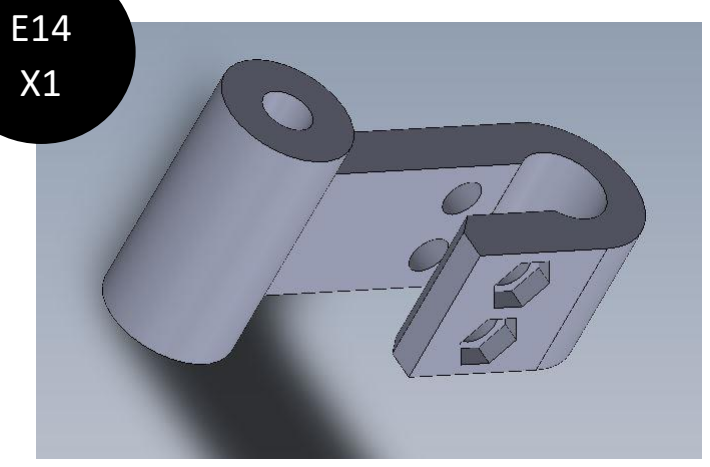
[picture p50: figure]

## Z emergency stop

D20
X3

D21
X3

D11
X3 | A5
| X4

D10
X1

# Z axis and X carriage: Parts

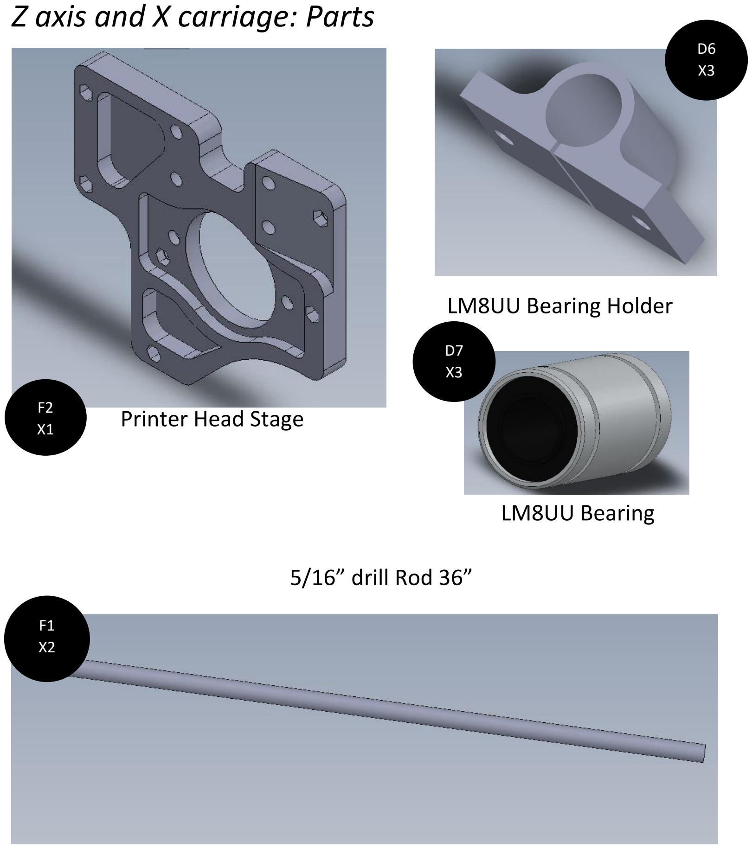
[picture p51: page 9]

## Printer Head Stage

## LM8UU Bearing

F2
X1

F1
X2

## 5/16” drill Rod 36”

## LM8UU Bearing Holder

D6
X3

D7
X3

Z axis and X carriage: Parts Contd.

## M3 X 16mm Bolt

## M3 Washer

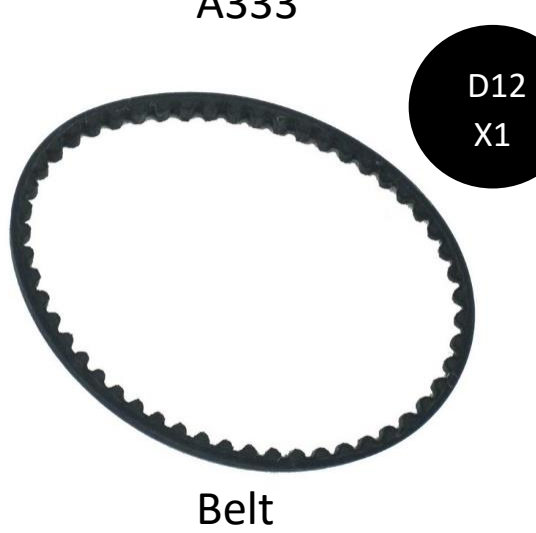
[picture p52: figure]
Belt

A333 | Y Belt Clamp

X10

D21
X10

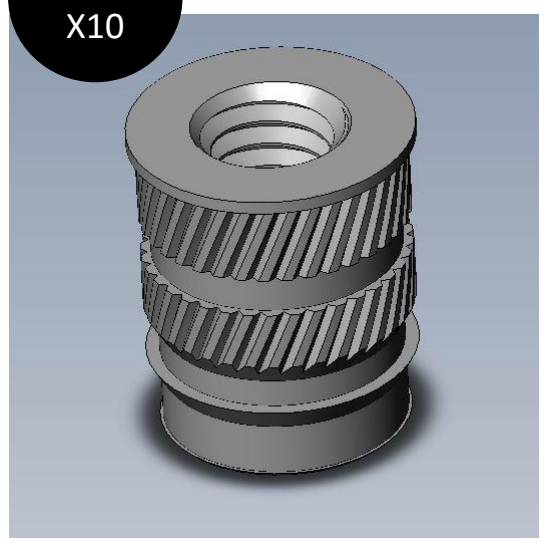
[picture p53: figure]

F3

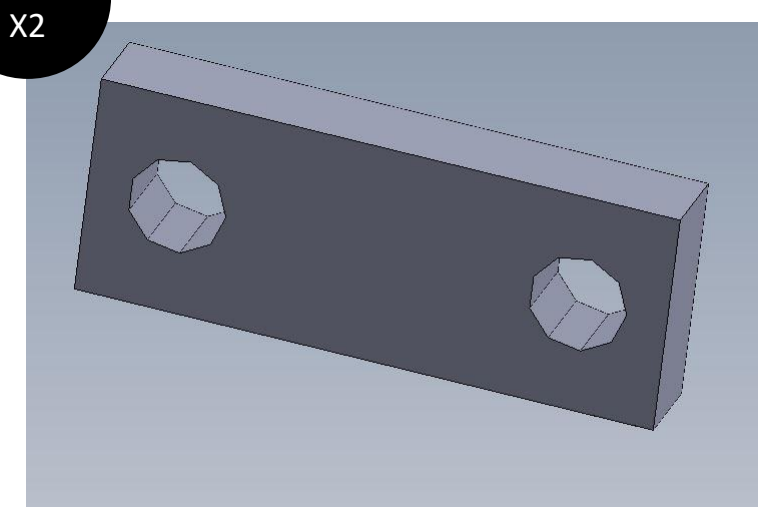
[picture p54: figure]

D14

# A - Y Axis Motor Mount Assembly

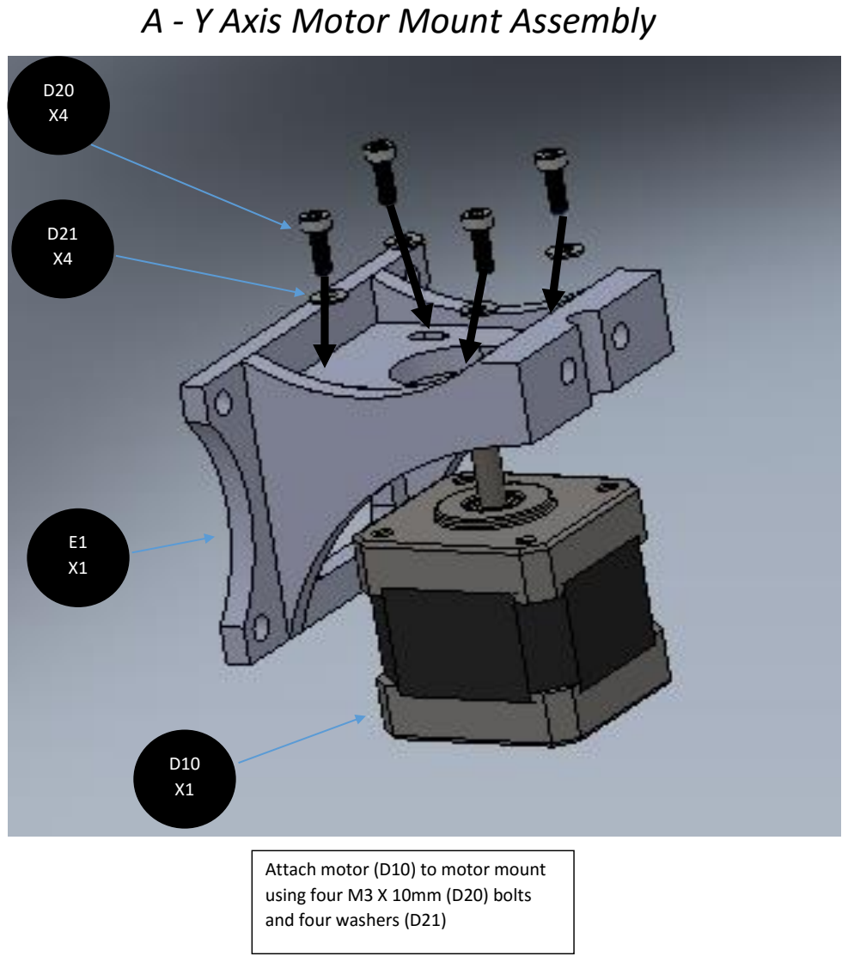
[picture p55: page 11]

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
Attach motor (D10) to motor mount using four M3 X 10mm (D20) bolts and four washers (D21)

# B – Y Axis motor mount Assembly

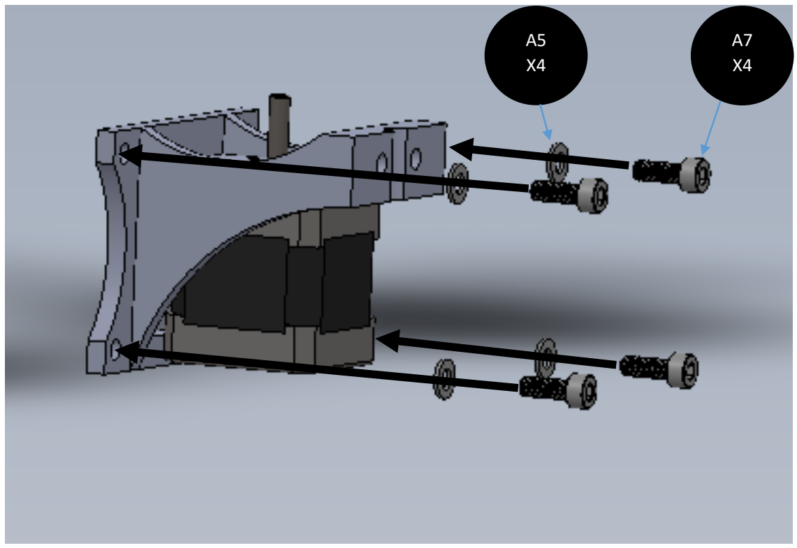
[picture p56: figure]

Attach motor mount and motor to the frame assembly using four M5 X 14mm (A7) bolts and four M5 washers (A5)

# C – No motor X End Clamp Assembly

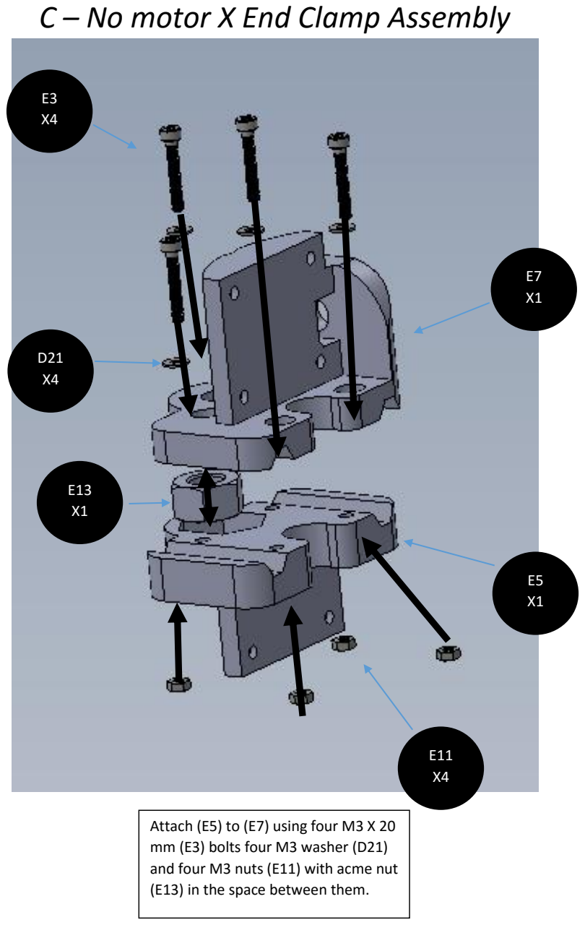
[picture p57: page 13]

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
Attach (E5) to (E7) using four M3 X 20 mm (E3) bolts four M3 washer (D21) and four M3 nuts (E11) with acme nut (E13) in the space between them.

# D – Non motor clamp bearing Assembly

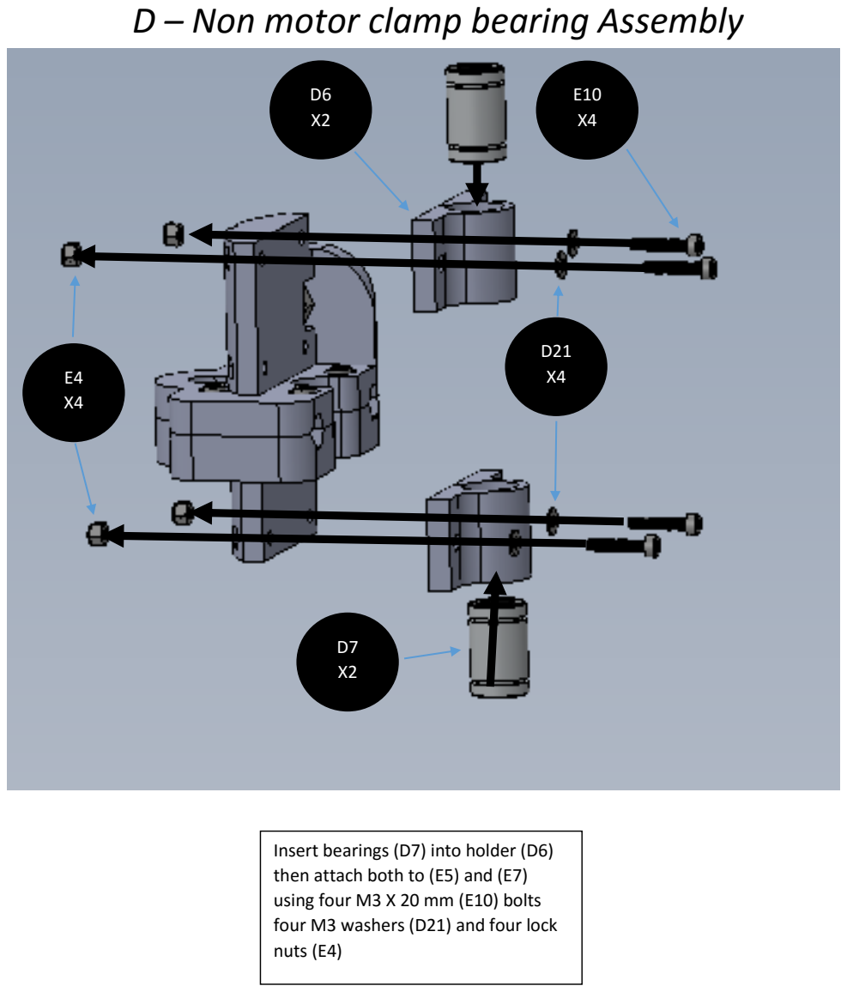
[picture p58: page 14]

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
Insert bearings (D7) into holder (D6) then attach both to (E5) and (E7) using four M3 X 20 mm (E10) bolts four M3 washers (D21) and four lock nuts (E4)

# E – Non motor Belt Bearings Assembly

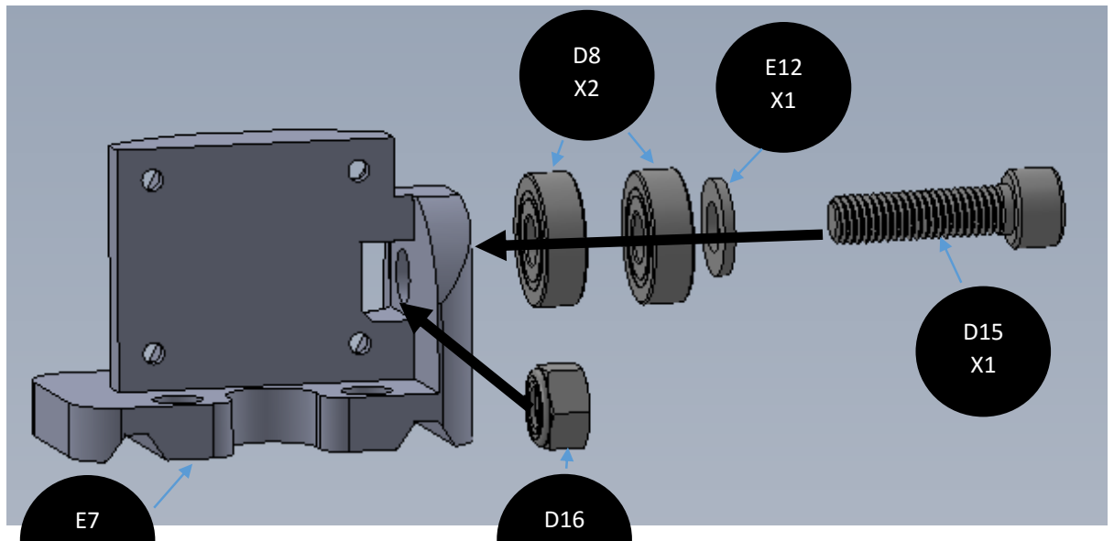
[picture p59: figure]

X1
X1

Attach bolt (D15) to (E7) using a washer (E12) and two bearings (D8) securing with lock nut (D16)

# F – Motor End Rod Clamp Assembly

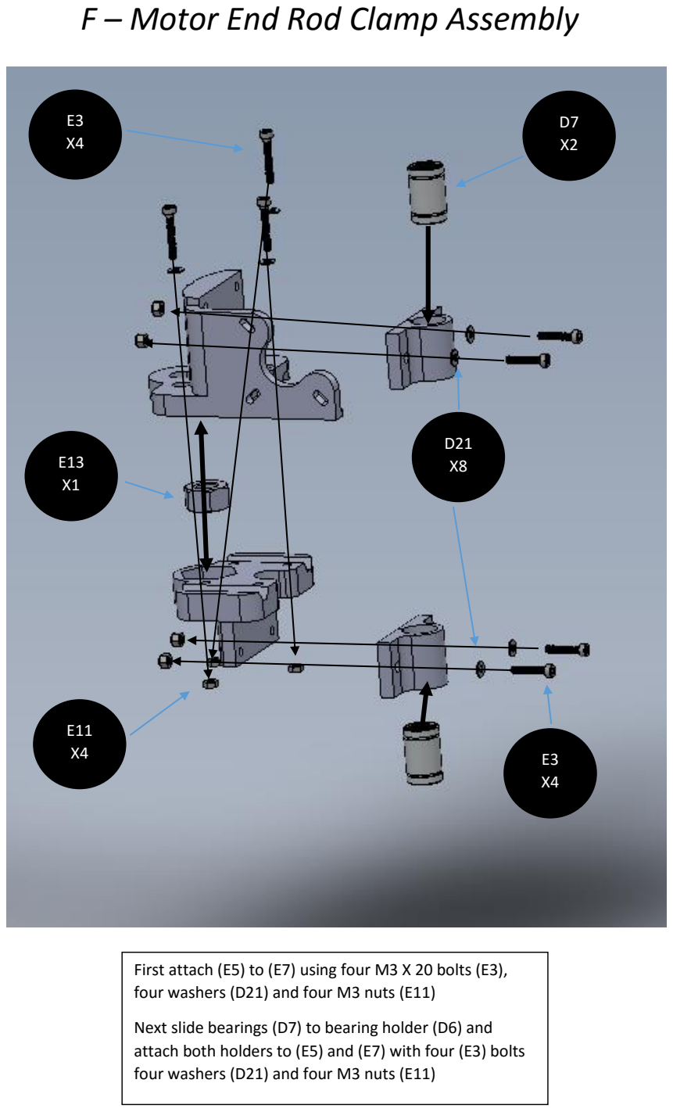
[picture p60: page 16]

First attach (E5) to (E7) using four M3 X 20 bolts (E3), four washers (D21) and four M3 nuts (E11)

Next slide bearings (D7) to bearing holder (D6) and attach both holders to (E5) and (E7) with four (E3) bolts four washers (D21) and four M3 nuts (E11)

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
# G – Motor End Motor Assembly

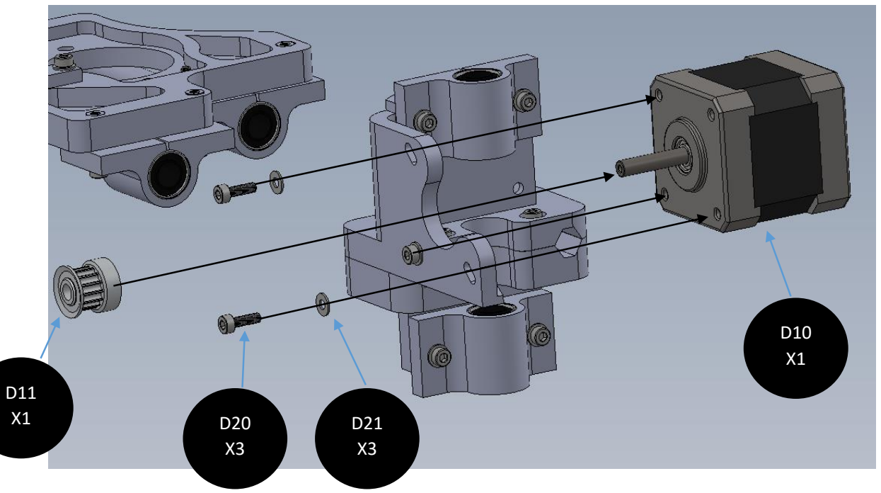
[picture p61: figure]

Attach motor (D10) to assembly with two (D20) bolts and two M3 washers (D21)

Next slide (D11) onto motor axle and secure with hex nut

# H- Y Axis Motor Rod Assembly

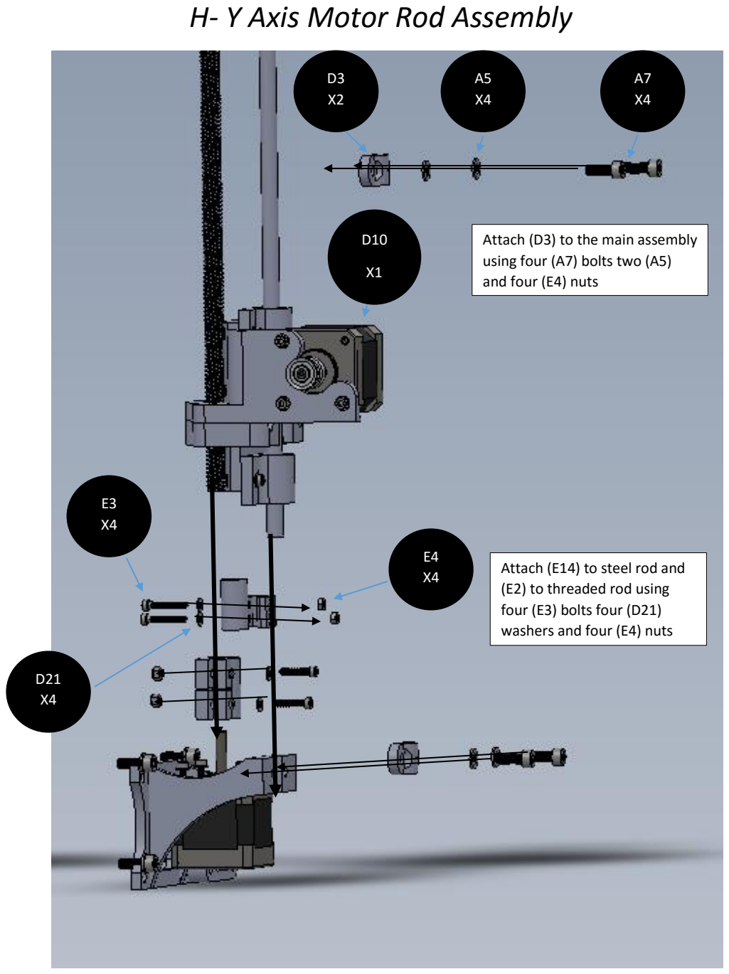
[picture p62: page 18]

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
Attach (D3) to the main assembly using four (A7) bolts two (A5) and four (E4) nuts

Attach (E14) to steel rod and (E2) to threaded rod using four (E3) bolts four (D21) washers and four (E4) nuts

# I - Y axis non motor Rod assembly

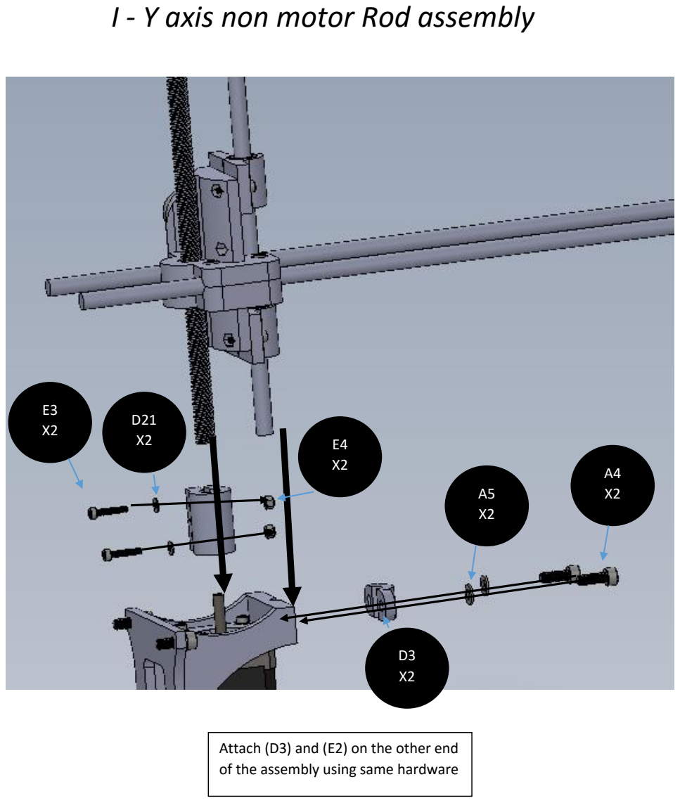
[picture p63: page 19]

D21
X2

E3
X2
E4
X2 | A4
| X2

D3
X2

A5
X2

Attach (D3) and (E2) on the other end of the assembly using same hardware

# J - X Carriage Assembly

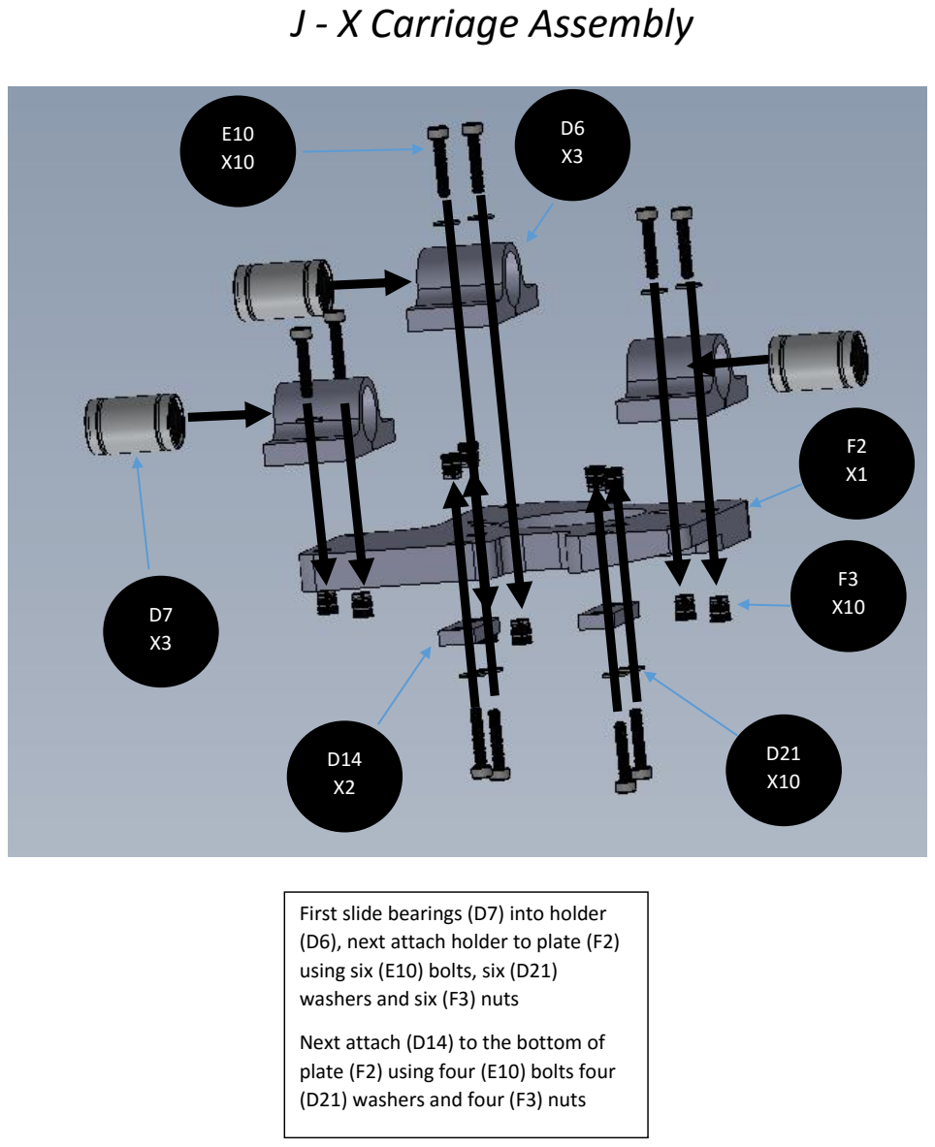
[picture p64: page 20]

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
First slide bearings (D7) into holder (D6), next attach holder to plate (F2) using six (E10) bolts, six (D21) washers and six (F3) nuts

Next attach (D14) to the bottom of plate (F2) using four (E10) bolts four (D21) washers and four (F3) nuts

# K - X Carriage Rod assembly

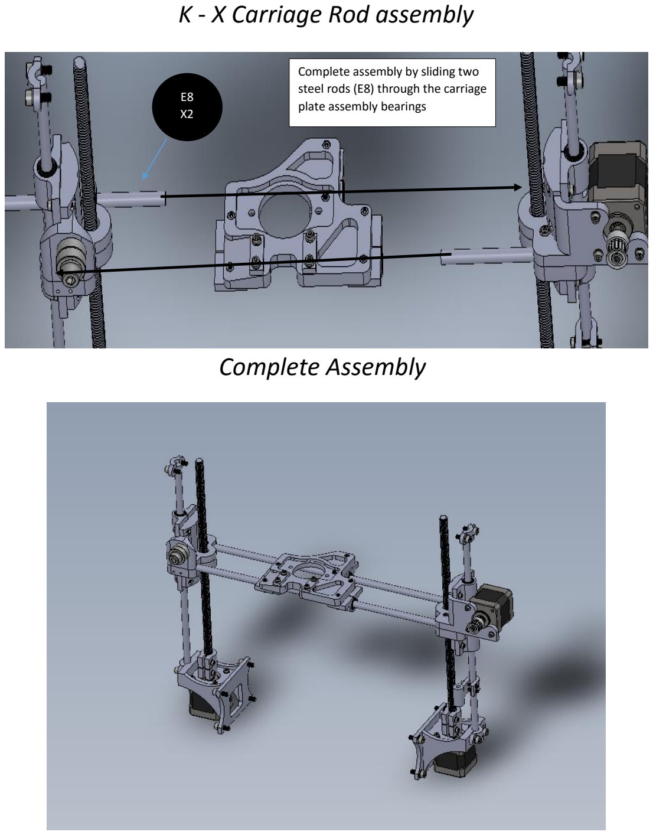
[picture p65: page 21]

# Complete Assembly

E8
X2

Complete assembly by sliding two steel rods (E8) through the carriage plate assembly bearings

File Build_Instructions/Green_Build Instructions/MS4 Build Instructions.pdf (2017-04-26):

## J - Extruder: Gear Box Sub-Assembly

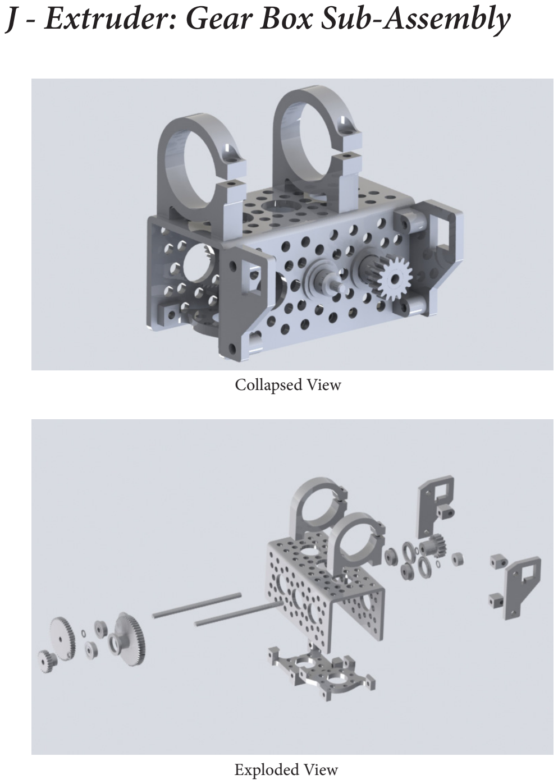
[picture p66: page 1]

Collapsed View

Exploded View

## J - Extruder: Extruder Arm Sub-Assembly

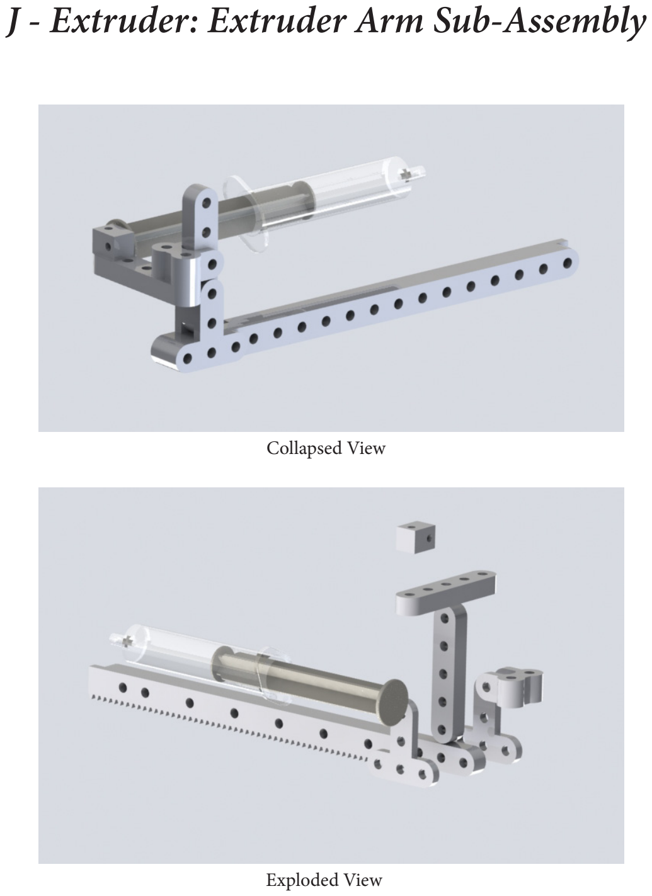
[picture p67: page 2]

Collapsed View

Exploded View

## J - Extruder: Motor Sub-Assembly

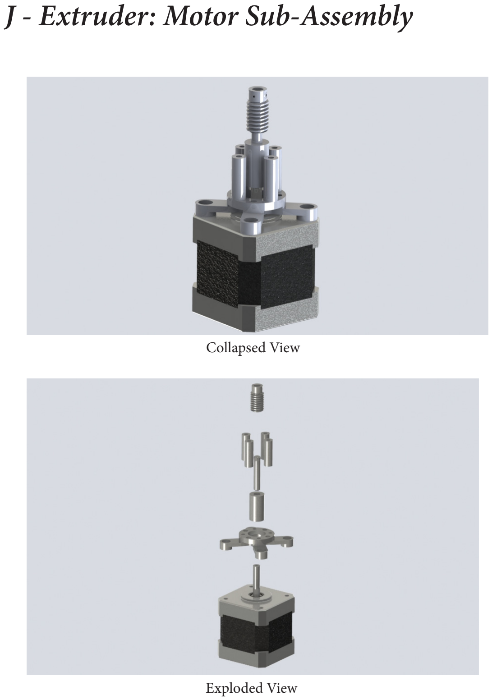
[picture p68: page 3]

Collapsed View

Exploded View

## J - Extruder: Complete Assembly


Collapsed View

Exploded View

## J - Extruder: Assembly Instructions

Gear Box Sub-Assembly

1. Find main gear box frame (J1) and orient as indicated.
2. Attach two 1” tube clamps (J15) using four 6-32 x 1/8” bolts.
3. Thread the first 2.375” shaft (J7) through holes 1 and 2 in the gearbox. On the hole 1 side of the shaft, place the 1/8” x 3/8” OD flanged ball bearing (J4), followed by the 0.375” center hole adapter, followed by a 0.016” washer (J9). Finally, place the 32DP, 16 toothed spur gear (J11) on the shaft.
4. Move the shaft (J7) placed through hole 1 so its now through hole 2. On the hole 2 side of the shaft, attach the 1/8” x 3/8” OD flanged ball bearing (J4), followed by the 0.375” center hole adapter, followed by the 0.016” washer (J9). Finally, place the 48DP, 48 toothed spur gear (J6) on the shaft.
5. Once the shaft has been centered through holes 1 and 2, tighten the two spur gears attached in steps 3 and 4. Make sure that there is no lateral movement in the shaft.
6. Place the 32DP, 100 toothed inner gear (J2) inside the gearbox and thread the second 2.375” shaft (J7) through hole 3, then the gear, then hole 4. (Note: the orientation of this inner gear (J2) does not matter as long as it lines up with the worm gear later in the assembly.)
7. On the hole 3 side of the shaft, attach the 1/8” x 3/8” OD flanged ball bearing (J4), followed by the 0.375” center hole adapter, followed by the 0.016” washer (J9). Finally, place the 1/8” shaft collar on the shaft.
8. On the hole 4 side of the shaft, attach the 1/8” x 3/8” OD flanged ball bearing (J4), followed by the 0.375” center hole adapter, followed by the 0.031” washer (J10). Finally, attach the 48DP, 24 toothed spur gear (J5).

## J - Extruder: Assembly Instructions

9. To attach the hub mount (J12), first notch out as shown and attach with three 6-32 ¼” bolts.
10. To attach the quad mount (J16), first notch out as shown and attach with three 6-32 ¼” bolts.
11. To attach the beam brackets (J13),
first attach beam blocks (J14)
to the gearbox as shown using three 6-32 1/8” bolt, then attach the beam brackets (J13) to the blocks (J14) using four 6-32 ½” bolts. To attach the final beam blocks (J14) to the gearbox, place two 6-32 ½” bolts through the quad and hub mounts (J12, J16), though the gearbox holes indicated, and into the gear blocks (J14).
Extruder Arm Sub-Assembly
1. On one end of the 6.16 aluminum beam (J22) attach the beam bracket F (J20) using two 6 – 32 x ¾ inch bolts,
two standard washers and two 6-32 nylock nuts
2. Attach the 1.54 aluminum beam (18) to the to the beam bracket F (J20) using two 6-32 x ¾ inch bolts. Two standard washers and two 6-32 nylock nuts.
3. The beam crossover adapter A (J19) should be connected to the 1.54 aluminum beam (J18) in the middle hole using one 6-32 x ¾ standard washer and a 6-32 nylock nut.
4. Add the next 1.54 aluminum beam (J18) to the assembly by attaching it perpendicularly to the beam crossover
adapter A (J19) with two 6-32 X 7/8 inch bolts two standard washers and two 6-32 nylock nuts

## J - Extruder: Assembly Instructions

5. Attachment block (J17), should be secured to the end of the 1.54 aluminum beam (J18) that was just attached in
step 4 using a 6-32 x ½ inch bolt and a 3mm washer the threaded hole on the attachment block A will serve as a nut for a bolt.
6. Use a dremel to cut the black plastic railing (J23) to about 5 ¼ inches.
7. Attach the black plastic railing (J24) to the 6.16 inch aluminum beam (J23) using three 6-32 x ¾ bolts two standard washers and two 6-32 nylock nuts, attach the bolts after they are already inserted into the Gear box, they will not fit into the space if the plastic railing is attached first. Motor Sub-Assembly
1. Attach the NEMA 17 motor mount (J25) to the NEMA 17 motor (D10) using the four set screws contained within.
2. Attach four 6-32 aluminum standoffs (H4) using four 1/2’’ 6-32 screws to the top of the NEMA 17 motor mount (J25).
3. Attach the 5 mm x 3/16’’ coupling (J26) to the drive shaft of the motor (D10) through the center of the mount (J25).
4. Insert the 3/16” shafting (J27) into the coupling (J2).
5. Attach the worm gear (J28) to the end of the shafting (J27).

## J - Extruder: Assembly Instructions

Complete Assembly

1. To attach the motor assembly to the gearbox, bolt the aluminum shafting (J27) to the hub mount (J12) as depicted. Note: Make sure the inner gear (J2) is aligned with the worm gear before attaching the motor mount to the gearbox.
2. Line up a 0.375” center hole adapters (J3) with the
1/8” ID x 3/8 “ OD flanged ball bearing (J4) and a thin 0.12” washer (J9) on the large center hole of the
3” aluminum channel (J1). Align the large gold gear (J2) in the center of the aluminum channel (J3), then slide the 0.12 x 2.3” rod (J7) through the aligned parts and anchor the end of the rod with the 0.3” round lock. Slide a 0.375” center hole adapter (J3) and 1/8” ID x 3/8” OD flanged ball bearing (J4) and a thin 0.12” washer (J9) onto the opposite end of the rod (J7) and anchor it with the small aluminum gear (J5). The end of the rod anchored with the smaller aluminum gear should be on the side of the 3” aluminum channel such that its opposite of the bolted side of the 1” bore tube clamp (J15).

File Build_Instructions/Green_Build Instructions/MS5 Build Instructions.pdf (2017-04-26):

# I - Wiring Harnesses: Parts

I1 ×1


Cloth carbon fiber tube

I2 ×1

22 AWG Copper Wire

I3 ×3

Male 2 POS wire housing
connector

I4 ×2

Male 3 POS wire housing
connector

I5 ×1

Female 3 POS wire housing
connector

I6 ×3

Female 24-30 Gauge Crimp
Connector

I7 ×12

Male 24-30 Gauge Crimp
Connector

I8 ×1

Plastic tubing

I9 ×1

Carbon fiber sleeve brackets

I10 ×1

I11 ×3

Wire temperature Sensor

I12 ×1

Needle mount

I13 ×1

Heat bed

# I - Assembly of Carbon Fiber Tube

# I - Assembly of Carbon Fiber Tube (cont)


1 - Solder three wires to each temperature sensor, insert one into carbon fiber sleeve bracket with carbon fiber tube and a fourth, separate stripped wire. Use Epoxy
to hold everything in place.
I1 | I9

I11

I2

I2

2 - crimp and connect the
three soldered wires to a
Male 3 POS wire housing
connector

I7 ×2

I3
I4

I7 ×3

3 - crimp and connect the
separate wire, and one additional wire, to a Male 2 POS housing connector

I1

I10

I2

4 - Insert the other end of the carbon fiber tube into the other bracket with the additional wire from Step 3. Use Epoxy, once again, to hold everything in place.

I8

5 - insert plastic tube
into carbon fiber tube

# I - Assembly of Needle Mount

I2

1 - before beginning, carve a hole into the needle mount. This is where the wires will be placed.

I12

2 - Solder three wires to each temperature sensor, insert one into carbon fiber sleeve bracket with carbon fiber tube and a fourth, separate stripped wire

3 - Strip and wrap the separate wire around the tip of the needle mount and cover in silver paint. Use Epoxy to hold everything in place, avoiding the hole of the needle mount. in the needle mount.

I11
I2

I - Assembly of Needle Mount (cont) | I - Additional Steps


I7 ×2

I7 ×3

5 - crimp and connect the
three soldered wires to a
Male 3 POS wire housing
connector

4 - Crimp and connect the separate wire, and one additional wire, to a Male 2 POS housing connector I11

I2

1 - Solder three wires to
each temperature sensor

I7 ×3

3 - Crimp and connect three separate wires to a female 2 POS housing connector

I4

I7 ×3

2 - crimp and connect
the three soldered
wires to a Male 3 POS
wire housing connector

I15

I13

I3 | I7 ×2

I3

I2

3 - solder two separate
wires to the heating
pad.

4 - Crimp and connect the two wires to
a Male 3 POS wire
housing connector

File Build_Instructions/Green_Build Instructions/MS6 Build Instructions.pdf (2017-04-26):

## H - Stage Plate: Parts


H2 ×2

H3 ×8

H4 ×4

A4 ×4 D19 ×4 | A5 ×4

Large Stage Plate

Small Stage Plate

Spring

Spacer

M5 Nut | M5 x 45 mm Bolt | M5 Washer

H5 ×8
| 6-32 x 1 inch Bolt

H1 ×1

## H - Stage Plate: Assembly


Exploded View 1

Exploded View 2

## H - Stage Plate: Assembly Instructions


Collapsed View

1. Fix large stage plate (H1) to existing base stage plate (D10) using 4 of the M5 bolts (A4), spacers (H4), M5 washers (A5), and M5 nuts (D19).
2. Attach two small stage plates (H2) to any of the 12 different locations on top of the large stage plate (H1) using 8 of the 6-32 bolts (H5) and springs (H3).

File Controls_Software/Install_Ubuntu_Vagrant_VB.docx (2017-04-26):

Video - https://vimeo.com/161519487

- Password: BIOE3090

Prerequisite:

Git - linux

Winggit - windows

1. Download and install precompiled VirtualBox executable as an administrator

(Right click→Run As Administrator) – windows, linux just run

2. Download and install precompiled Vagrant executable as an administrator

(Right click→Run As Administrator) – windows, linux just run

3. Create directory where you would like to store software using the command line

(cd, ls, mkdir) - linux

(cd, dir, mkdir) - windows

4. Download Vagrant files from github

git clone https://github.com/UCDBioe/printer_VM.git

5. Package.box file is too large for github account – will be provided during class
6. Navigate to directory containing box file

5. Add the box using vagrant

vagrant box add –name Ubuntu_14.04_64 package.box

6. Build the Virtual environment

a. Navigate to directory containing Vagrantfile

vagrant up

7. WAIT!!! – wait until completed

8. At process completion, as judged by terminal status, log into Ubuntu

Username: vagrant

Password: vagrant

9. Verify Configuration

python –version

Output: Python 3.5.1 :: Anaconda 2.5.0 (64-bit)

10. Check what anaconda environments are on the system

a. conda info --envs
b. activate environment

source activate YourENvname

c. deactivate environment

source deactivate

# USB Port pass through

USB ports will need to be passed through the virtual machine for Ubuntu to have access to the ports.

10. Pass ports from host OS to Virtual box

  a. Right click on icon below


  b. Select port of interest
  c. Repeat for other ports
d. Identify port numbers in virtual environment using arduino
e. Edit GUI python lines for port names using vim and save

ser=ser.serial(portname,baudrate)

f. Verify installation by running Bioprinter_Cotrols_GUI while connected to the printer

Python BioPrinter_Controls_GUI.py

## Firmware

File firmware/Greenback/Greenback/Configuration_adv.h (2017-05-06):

#ifndef CONFIGURATION_ADV_H
#define CONFIGURATION_ADV_H

//===========================================================================
//=============================Thermal Settings  ============================
//===========================================================================

#ifdef BED_LIMIT_SWITCHING
  #define BED_HYSTERESIS 2 //only disable heating if T>target+BED_HYSTERESIS and enable heating if T>target-BED_HYSTERESIS
#endif
#define BED_CHECK_INTERVAL 5000 //ms between checks in bang-bang control

//// Heating sanity check:
// This waits for the watch period in milliseconds whenever an M104 or M109 increases the target temperature
// If the temperature has not increased at the end of that period, the target temperature is set to zero.
// It can be reset with another M104/M109. This check is also only triggered if the target temperature and the current temperature
//  differ by at least 2x WATCH_TEMP_INCREASE
//#define WATCH_TEMP_PERIOD 40000 //40 seconds
//#define WATCH_TEMP_INCREASE 10  //Heat up at least 10 degree in 20 seconds

#ifdef PIDTEMP
  // this adds an experimental additional term to the heating power, proportional to the extrusion speed.
  // if Kc is chosen well, the additional required power due to increased melting should be compensated.
  #define PID_ADD_EXTRUSION_RATE
  #ifdef PID_ADD_EXTRUSION_RATE
    #define  DEFAULT_Kc (1) //heating power=Kc*(e_speed)
  #endif
#endif


//automatic temperature: The hot end target temperature is calculated by all the buffered lines of gcode.
//The maximum buffered steps/sec of the extruder motor are called "se".
//You enter the autotemp mode by a M109 S<mintemp> B<maxtemp> F<factor>
// the target temperature is set to mintemp+factor*se[steps/sec] and limited by mintemp and maxtemp
// you exit the value by any M109 without F*
// Also, if the temperature is set to a value <mintemp, it is not changed by autotemp.
// on an Ultimaker, some initial testing worked with M109 S215 B260 F1 in the start.gcode
#define AUTOTEMP
#ifdef AUTOTEMP
  #define AUTOTEMP_OLDWEIGHT 0.98
#endif

//Show Temperature ADC value
//The M105 command return, besides traditional information, the ADC value read from temperature sensors.
//#define SHOW_TEMP_ADC_VALUES

//  extruder run-out prevention.
//if the machine is idle, and the temperature over MINTEMP, every couple of SECONDS some filament is extruded
//#define EXTRUDER_RUNOUT_PREVENT
#define EXTRUDER_RUNOUT_MINTEMP 190
#define EXTRUDER_RUNOUT_SECONDS 30.
#define EXTRUDER_RUNOUT_ESTEPS 14. //mm filament
#define EXTRUDER_RUNOUT_SPEED 1500.  //extrusion speed
#define EXTRUDER_RUNOUT_EXTRUDE 100

//These defines help to calibrate the AD595 sensor in case you get wrong temperature measurements.
//The measured temperature is defined as "actualTemp = (measuredTemp * TEMP_SENSOR_AD595_GAIN) + TEMP_SENSOR_AD595_OFFSET"
#define TEMP_SENSOR_AD595_OFFSET 0.0
#define TEMP_SENSOR_AD595_GAIN   1.0

//This is for controlling a fan to cool down the stepper drivers
//it will turn on when any driver is enabled
//and turn off after the set amount of seconds from last driver being disabled again
#define CONTROLLERFAN_PIN -1 //Pin used for the fan to cool controller (-1 to disable)
#define CONTROLLERFAN_SECS 60 //How many seconds, after all motors were disabled, the fan should run
#define CONTROLLERFAN_SPEED 255  // == full speed

// When first starting the main fan, run it at full speed for the
// given number of milliseconds.  This gets the fan spinning reliably
// before setting a PWM value. (Does not work with software PWM for fan on Sanguinololu)
//#define FAN_KICKSTART_TIME 100

// Extruder cooling fans
// Configure fan pin outputs to automatically turn on/off when the associated
// extruder temperature is above/below EXTRUDER_AUTO_FAN_TEMPERATURE.
// Multiple extruders can be assigned to the same pin in which case
// the fan will turn on when any selected extruder is above the threshold.
#define EXTRUDER_0_AUTO_FAN_PIN   -1
#define EXTRUDER_1_AUTO_FAN_PIN   -1
#define EXTRUDER_2_AUTO_FAN_PIN   -1
#define EXTRUDER_AUTO_FAN_TEMPERATURE 50
#define EXTRUDER_AUTO_FAN_SPEED   255  // == full speed


//===========================================================================
//=============================Mechanical Settings===========================
//===========================================================================

#define ENDSTOPS_ONLY_FOR_HOMING // If defined the endstops will only be used for homing


//// AUTOSET LOCATIONS OF LIMIT SWITCHES
//// Added by ZetaPhoenix 09-15-2012
#ifdef MANUAL_HOME_POSITIONS  // Use manual limit switch locations
  #define X_HOME_POS MANUAL_X_HOME_POS
  #define Y_HOME_POS MANUAL_Y_HOME_POS
  #define Z_HOME_POS MANUAL_Z_HOME_POS
#else //Set min/max homing switch positions based upon homing direction and min/max travel limits
  //X axis
  #if X_HOME_DIR == -1
    #ifdef BED_CENTER_AT_0_0
      #define X_HOME_POS X_MAX_LENGTH * -0.5
    #else
      #define X_HOME_POS X_MIN_POS
    #endif //BED_CENTER_AT_0_0
  #else
    #ifdef BED_CENTER_AT_0_0
      #define X_HOME_POS X_MAX_LENGTH * 0.5
    #else
      #define X_HOME_POS X_MAX_POS
    #endif //BED_CENTER_AT_0_0
  #endif //X_HOME_DIR == -1

  //Y axis
  #if Y_HOME_DIR == -1
    #ifdef BED_CENTER_AT_0_0
      #define Y_HOME_POS Y_MAX_LENGTH * -0.5
    #else
      #define Y_HOME_POS Y_MIN_POS
    #endif //BED_CENTER_AT_0_0
  #else
    #ifdef BED_CENTER_AT_0_0
      #define Y_HOME_POS Y_MAX_LENGTH * 0.5
    #else
      #define Y_HOME_POS Y_MAX_POS
    #endif //BED_CENTER_AT_0_0
  #endif //Y_HOME_DIR == -1

  // Z axis
  #if Z_HOME_DIR == -1 //BED_CENTER_AT_0_0 not used
    #define Z_HOME_POS Z_MIN_POS
  #else
    #define Z_HOME_POS Z_MAX_POS
  #endif //Z_HOME_DIR == -1
#endif //End auto min/max positions
//END AUTOSET LOCATIONS OF LIMIT SWITCHES -ZP


//#define Z_LATE_ENABLE // Enable Z the last moment. Needed if your Z driver overheats.

// A single Z stepper driver is usually used to drive 2 stepper motors.
// Uncomment this define to utilize a separate stepper driver for each Z axis motor.
// Only a few motherboards support this, like RAMPS, which have dual extruder support (the 2nd, often unused, extruder driver is used
// to control the 2nd Z axis stepper motor). The pins are currently only defined for a RAMPS motherboards.
// On a RAMPS (or other 5 driver) motherboard, using this feature will limit you to using 1 extruder.
//#define Z_DUAL_STEPPER_DRIVERS

#ifdef Z_DUAL_STEPPER_DRIVERS
  #undef EXTRUDERS
  #define EXTRUDERS 1
#endif

// Same again but for Y Axis.
//#define Y_DUAL_STEPPER_DRIVERS

// Define if the two Y drives need to rotate in opposite directions
#define INVERT_Y2_VS_Y_DIR true

#ifdef Y_DUAL_STEPPER_DRIVERS
  #undef EXTRUDERS
  #define EXTRUDERS 1
#endif

#if defined (Z_DUAL_STEPPER_DRIVERS) && defined (Y_DUAL_STEPPER_DRIVERS)
  #error "You cannot have dual drivers for both Y and Z"
#endif

// Enable this for dual x-carriage printers.
// A dual x-carriage design has the advantage that the inactive extruder can be parked which
// prevents hot-end ooze contaminating the print. It also reduces the weight of each x-carriage
// allowing faster printing speeds.
//#define DUAL_X_CARRIAGE
#ifdef DUAL_X_CARRIAGE
// Configuration for second X-carriage
// Note: the first x-carriage is defined as the x-carriage which homes to the minimum endstop;
// the second x-carriage always homes to the maximum endstop.
#define X2_MIN_POS 80     // set minimum to ensure second x-carriage doesn't hit the parked first X-carriage
#define X2_MAX_POS 353    // set maximum to the distance between toolheads when both heads are homed
#define X2_HOME_DIR 1     // the second X-carriage always homes to the maximum endstop position
#define X2_HOME_POS X2_MAX_POS // default home position is the maximum carriage position
    // However: In this mode the EXTRUDER_OFFSET_X value for the second extruder provides a software
    // override for X2_HOME_POS. This also allow recalibration of the distance between the two endstops
    // without modifying the firmware (through the "M218 T1 X???" command).
    // Remember: you should set the second extruder x-offset to 0 in your slicer.

// Pins for second x-carriage stepper driver (defined here to avoid further complicating pins.h)
#define X2_ENABLE_PIN 29
#define X2_STEP_PIN 25
#define X2_DIR_PIN 23

// There are a few selectable movement modes for dual x-carriages using M605 S<mode>
//    Mode 0: Full control. The slicer has full control over both x-carriages and can achieve optimal travel results
//                           as long as it supports dual x-carriages. (M605 S0)
//    Mode 1: Auto-park mode. The firmware will automatically park and unpark the x-carriages on tool changes so
//                           that additional slicer support is not required. (M605 S1)
//    Mode 2: Duplication mode. The firmware will transparently make the second x-carriage and extruder copy all
//                           actions of the first x-carriage. This allows the printer to print 2 arbitrary items at
//                           once. (2nd extruder x offset and temp offset are set using: M605 S2 [Xnnn] [Rmmm])

// This is the default power-up mode which can be later using M605.
#define DEFAULT_DUAL_X_CARRIAGE_MODE 0

// As the x-carriages are independent we can now account for any relative Z offset
#define EXTRUDER1_Z_OFFSET 0.0           // z offset relative to extruder 0

// Default settings in "Auto-park Mode"
#define TOOLCHANGE_PARK_ZLIFT   0.2      // the distance to raise Z axis when parking an extruder
#define TOOLCHANGE_UNPARK_ZLIFT 1        // the distance to raise Z axis when unparking an extruder

// Default x offset in duplication mode (typically set to half print bed width)
#define DEFAULT_DUPLICATION_X_OFFSET 100

#endif //DUAL_X_CARRIAGE

//homing hits the endstop, then retracts by this distance, before it tries to slowly bump again:
#define X_HOME_RETRACT_MM 5
#define Y_HOME_RETRACT_MM 5
#define Z_HOME_RETRACT_MM 2
//#define QUICK_HOME  //if this is defined, if both x and y are to be homed, a diagonal move will be performed initially.

#define AXIS_RELATIVE_MODES {false, false, false, false}
#ifdef CONFIG_STEPPERS_TOSHIBA
#define MAX_STEP_FREQUENCY 10000 // Max step frequency for Toshiba Stepper Controllers
#else
#define MAX_STEP_FREQUENCY 40000 // Max step frequency for Ultimaker (5000 pps / half step)
#endif
//By default pololu step drivers require an active high signal. However, some high power drivers require an active low signal as step.
#define INVERT_X_STEP_PIN false
#define INVERT_Y_STEP_PIN false
#define INVERT_Z_STEP_PIN false
#define INVERT_E_STEP_PIN false

//AR 5/6
#define INVERT_X2_STEP_PIN false
#define INVERT_Z2_STEP_PIN false

//default stepper release if idle
#define DEFAULT_STEPPER_DEACTIVE_TIME 60

#define DEFAULT_MINIMUMFEEDRATE       0.0     // minimum feedrate
#define DEFAULT_MINTRAVELFEEDRATE     0.0

// Feedrates for manual moves along X, Y, Z, E from panel
#ifdef ULTIPANEL
#define MANUAL_FEEDRATE {50*60, 50*60, 4*60, 60}  // set the speeds for manual moves (mm/min)
#endif

//Comment to disable setting feedrate multiplier via encoder
#ifdef ULTIPANEL
    #define ULTIPANEL_FEEDMULTIPLY
#endif

// minimum time in microseconds that a movement needs to take if the buffer is emptied.
#define DEFAULT_MINSEGMENTTIME        20000

// If defined the movements slow down when the look ahead buffer is only half full
#define SLOWDOWN

// Frequency limit
// See nophead's blog for more info
// Not working O
//#define XY_FREQUENCY_LIMIT  15

// Minimum planner junction speed. Sets the default minimum speed the planner plans for at the end
// of the buffer and all stops. This should not be much greater than zero and should only be changed
// if unwanted behavior is observed on a user's machine when running at very slow speeds.
#define MINIMUM_PLANNER_SPEED 0.05// (mm/sec)
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

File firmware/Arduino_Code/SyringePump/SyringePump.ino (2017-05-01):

/**************************
  Control the pump rate, acceleration and temperature controls for a syringe pump.
  The system works on a latching control where an external signal turns the pump
  on and off. When the pump is initially turned on, it will accelerate up to the 
  dispense rate. When the pump is turned off, it will not decelerate but will come
  to a complete stop.

  Stepper motor control is controlled by Timer1 ISR. Timer1 controls the servo() library
  in Arduino, so be aware that the servo()library will not function properly in this 
  program. So don't use that servo here!
  
  Eventually the pump rate and on/off signal will be set by commands sent over SPI.
***************************/

// IMPORTANT: Need to turn on BIO_SPI_SLAVE
// in order to include the correct headers and declarations
#define BIO_SPI_SLAVE 1


// ------- Flags ----------- //
#define ENABLE_PID_LOOP_G_CODE_CONTROL 0

// ------- Preamble -------- //
/* These parameters will depend on your motor, what it's driving */
#define SYRINGE_HEATER_PIN  6  // PWM pin for MOSFET control via PID
#define TUBE_HEATER_PIN     5  // PWM pin for MOSFET control via PID
#define BIO_INTERRUPT_PIN   2  // Pin for hardware interrupt signaling bioprint state
#define BIO_INTERRUPT_NUM   0  // Pin for hardware interrupt signaling bioprint state
#define STEPPER_DIR_PN      4  // Pin for setting extruder direction
#define STEPPER_STEP_PIN    8  //5//3// Pin for setting extruder steps to motor controller (any digital pin, does not need PWM)
#define MAX_TUBE_TEMP       45 // Max temperature for tube heater, so it does not melt
#if BP_CURRENT >= BP_ENDSTOP
  #define NEEDLE_HEATER_PIN   9  // PWM pin for MOSFET control via PID
  #define ENDSTOP_FULL_PIN    A0
  #define ISR_ENSTOP_PIN      3
#else
  #define NEEDLE_HEATER_PIN   3  // PWM pin for MOSFET control via PID
#endif

#include <PID_v1.h>
#include <OneWire.h>
#include <DallasTemperature.h>
#include <bioSPI.h>
#include "Temp_DS18B20.h"
#include "Pump_Stepper.h"
#include "Configuration.h"
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

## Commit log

2017-05-01 determined pins for x2, z2 motors, endstops
2017-05-04 added x2 and z2 pin values
2017-05-04 added print statements
2017-05-07 intialized axes pins in stepper.cpp
